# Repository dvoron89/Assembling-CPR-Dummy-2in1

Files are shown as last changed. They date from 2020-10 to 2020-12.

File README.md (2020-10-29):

# CPR-Dummy-2in1
Simulator for medical skill practicing and qualification improvement (CPR training)

Hello!
Here you can find manual for assembling CPR Dummy (look for full .doc version with images in Manual folder)

Note that you will need 3D printer (or someone who can print some models for you).

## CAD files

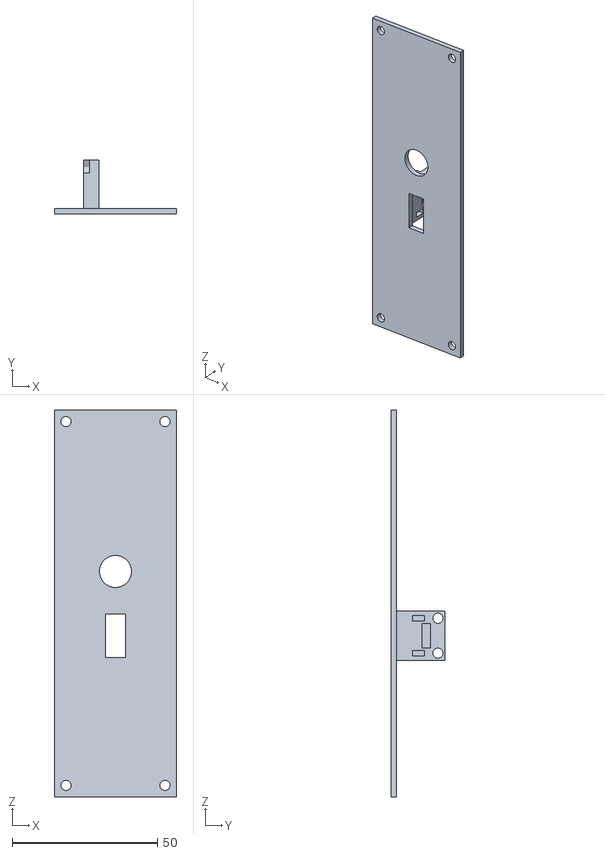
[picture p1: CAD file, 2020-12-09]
3D models to print/Large Cover (CPR195).stl
42.0 x 18.7 x 133.0

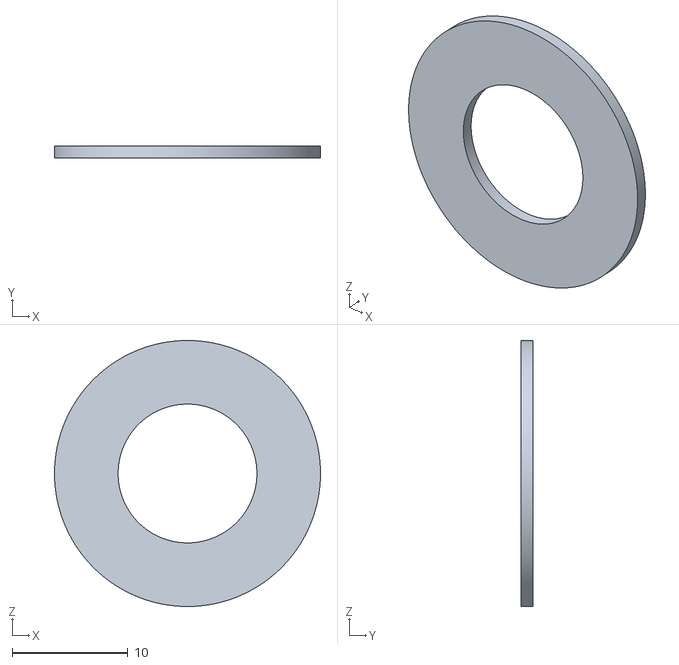
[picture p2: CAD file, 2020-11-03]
3D models to print/Inner DC Cover.stl
23.0 x 1.00 x 23.0

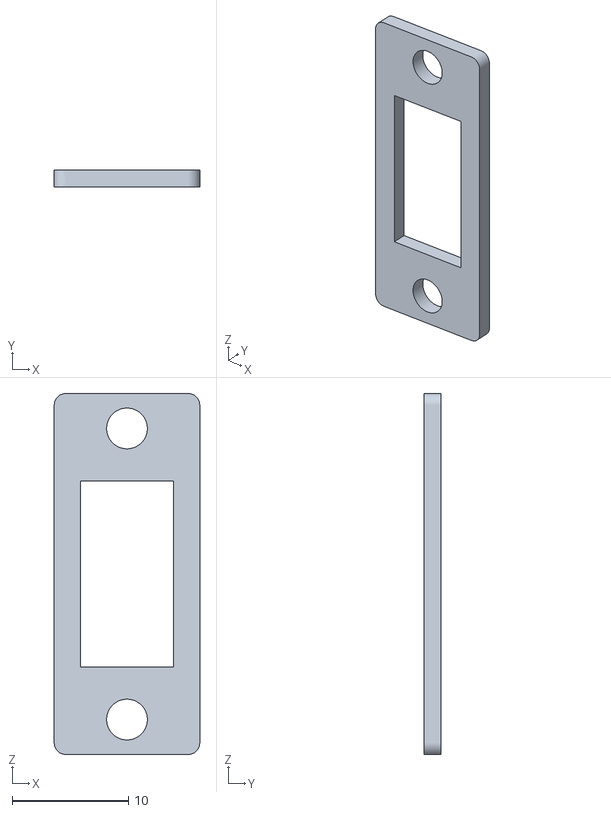
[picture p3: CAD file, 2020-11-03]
3D models to print/USB only Outer.stl
12.5 x 1.50 x 31.0

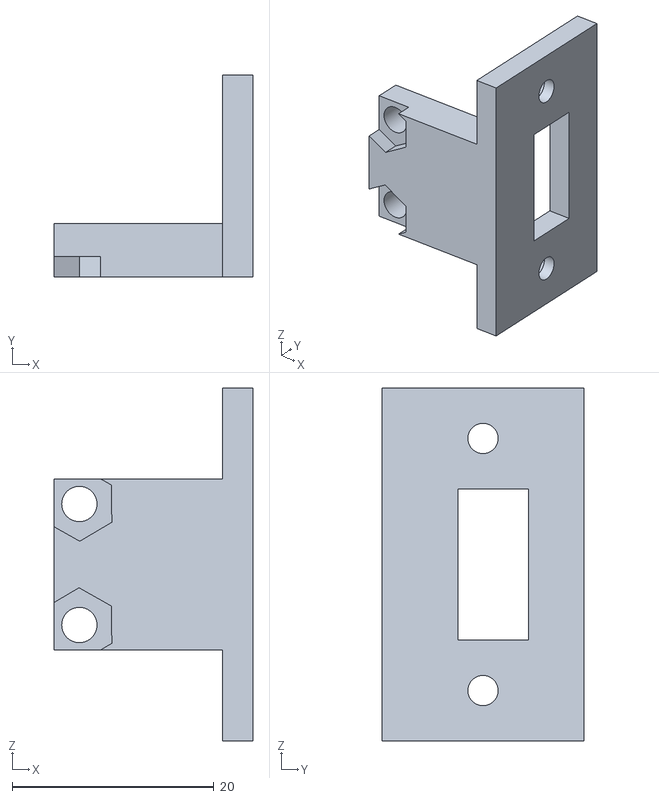
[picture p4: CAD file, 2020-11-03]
3D models to print/USB only Inner.stl
19.7 x 20.0 x 35.0

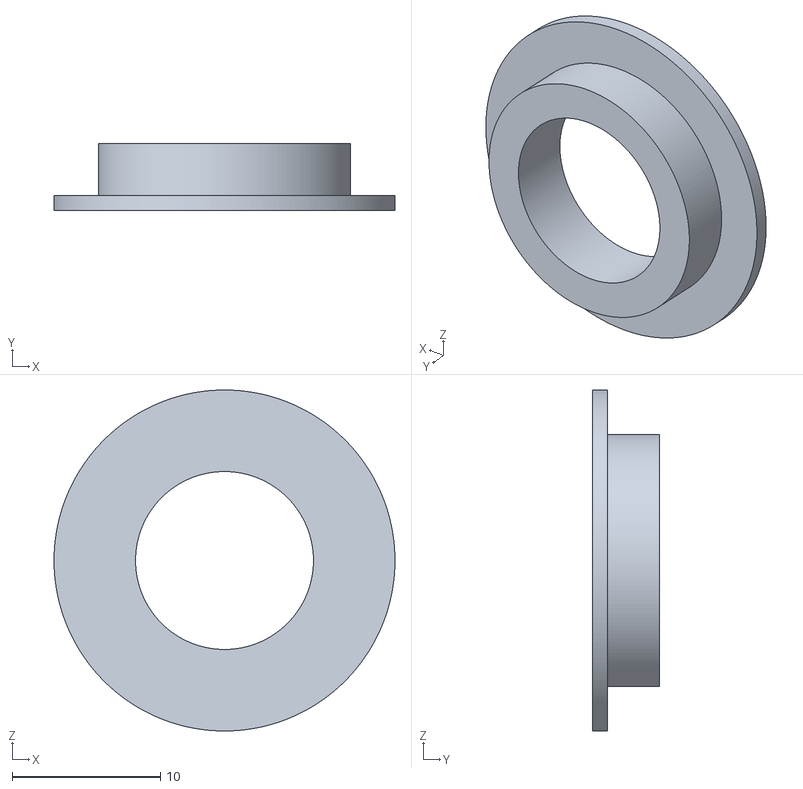
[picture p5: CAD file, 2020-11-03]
3D models to print/Outer DC Cover.stl
23.0 x 4.50 x 23.0

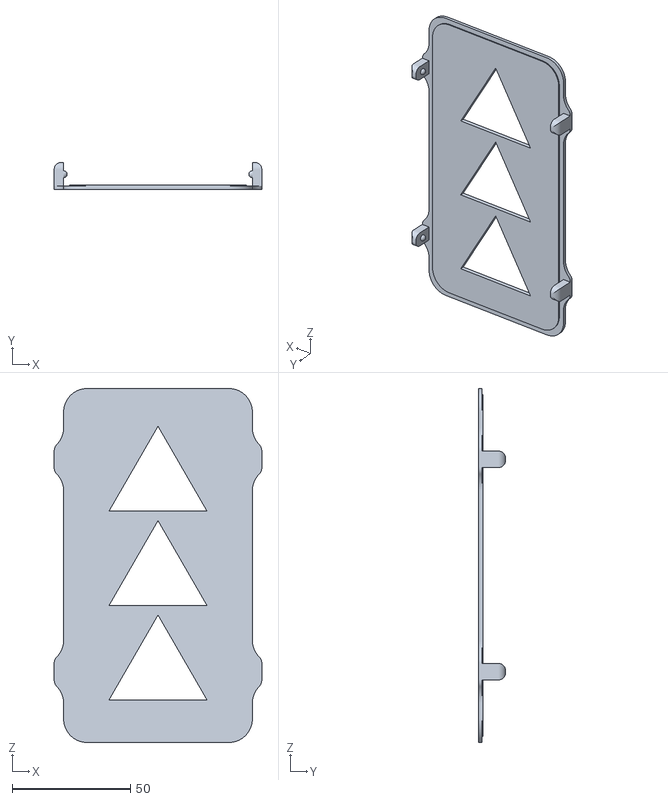
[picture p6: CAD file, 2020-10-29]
3D models to print/Custom Cover (All models).stl
88.0 x 11.5 x 150.0

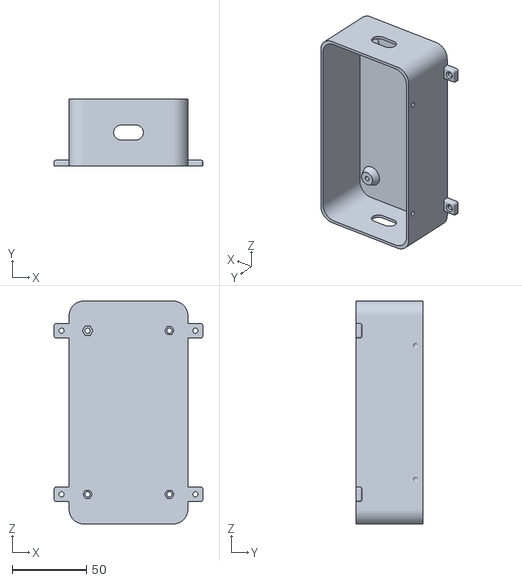
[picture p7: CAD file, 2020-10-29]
3D models to print/Case (All models).stl
100.0 x 45.0 x 150.0

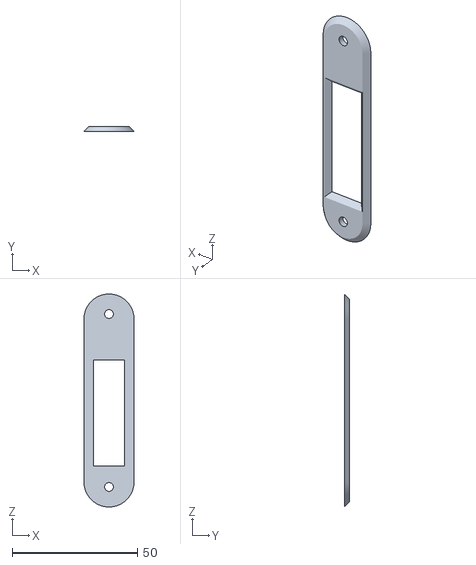
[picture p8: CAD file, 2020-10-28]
3D models to print/Outer Cover.stl
20.0 x 2.00 x 85.0

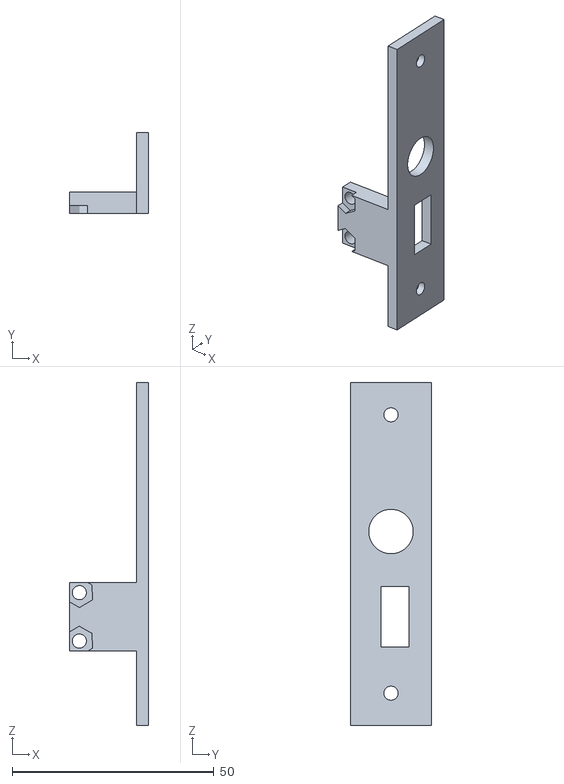
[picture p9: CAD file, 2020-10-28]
3D models to print/Inner Cover.stl
19.7 x 20.0 x 85.0

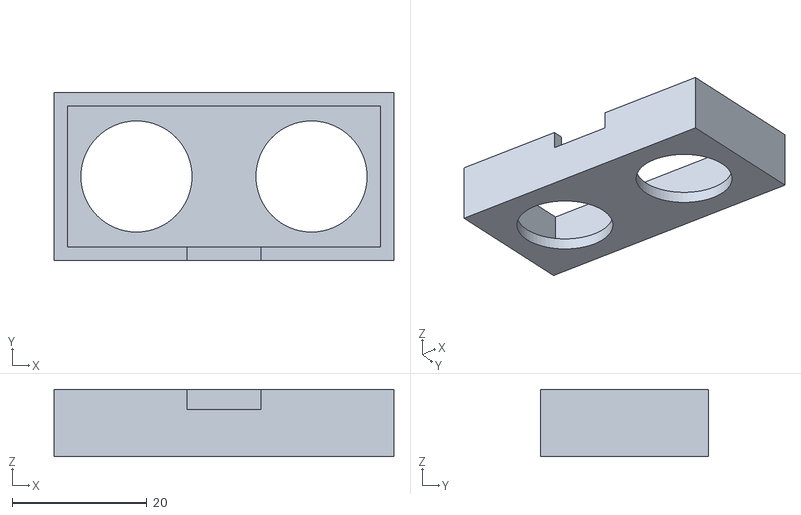
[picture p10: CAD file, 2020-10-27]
3D models to print/Sonar Case.stl
50.5 x 25.0 x 10.0

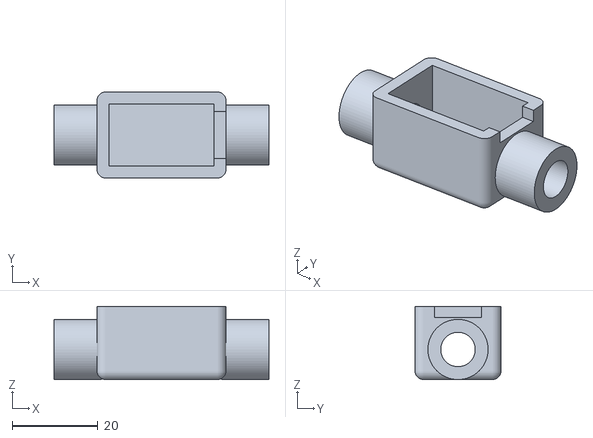
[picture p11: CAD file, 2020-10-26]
3D models to print/Pressure Sensor Case.stl
50.0 x 20.0 x 17.0

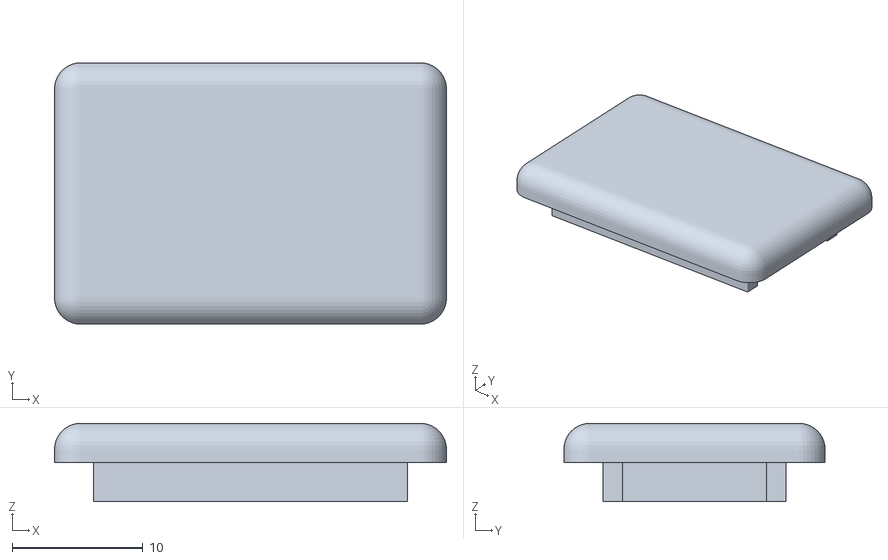
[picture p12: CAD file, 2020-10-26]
3D models to print/Pressure Sensor Cover.stl
30.0 x 20.0 x 6.00

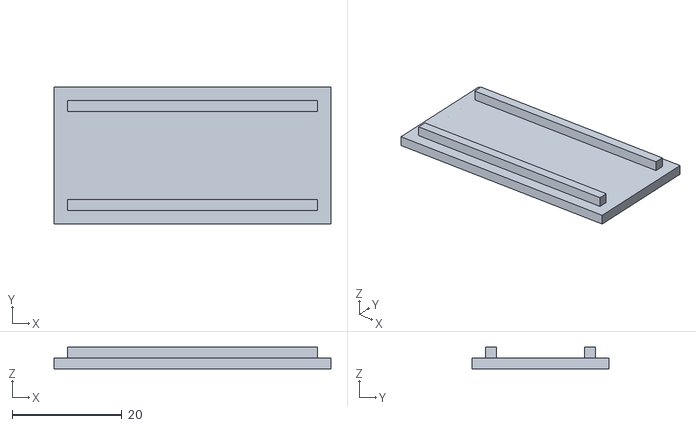
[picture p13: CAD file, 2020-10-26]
3D models to print/Sonar Cover.stl
50.5 x 25.0 x 4.00

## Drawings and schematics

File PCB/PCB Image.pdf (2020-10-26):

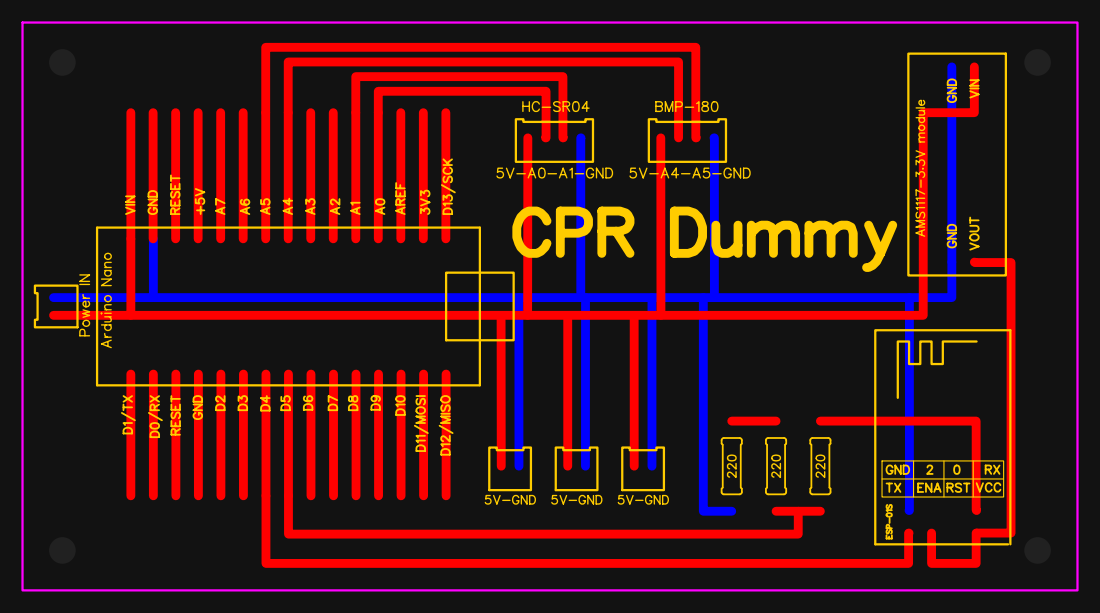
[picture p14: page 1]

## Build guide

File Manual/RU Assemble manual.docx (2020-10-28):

Инструкция по сборке симулятора для отработки СЛР с возможностью подключения к ПК по WIFI или USB кабелю

В качестве шасси применятся манекен модели CPR190 или CPR195 (предпочтительнее CPR190)

Разборка манекена:

1. Снять имитацию кожного покрова с торса манекена
2. Отсоединить трубку, имитирующую трахею/пищевод
3. Отключить все кабели, соединяющие шасси манекена с пластиной, имитирующей грудную клетку
4. Извлечь пластину, имитирующую грудную клетку из посадочного места на шасси манекена
5. При необходимости, снять имитацию кожного покрова с головы манекена и извлечь датчики из глаз и прочие электронные компоненты
6. Отключить все электронные компоненты внутри шасси манекена
7. Отсоединить и извлечь все электронные компоненты из шасси манекена
8. Извлечь перепускной клапан из разреза трубки, имитирующей трахею:

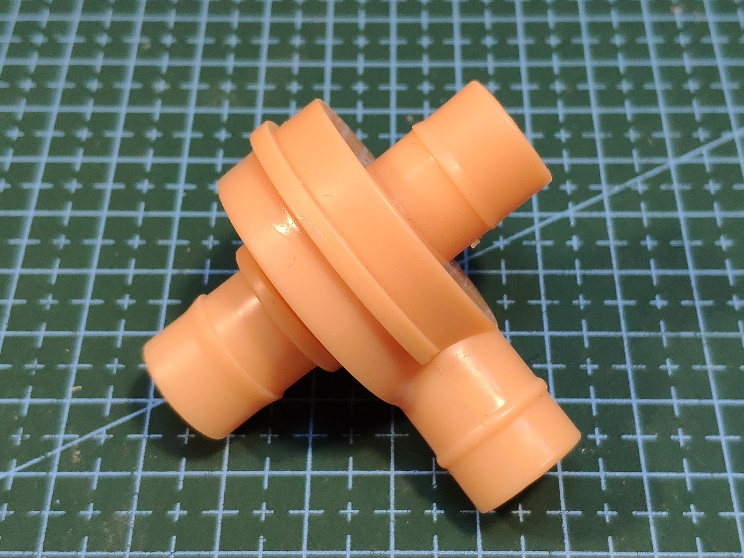
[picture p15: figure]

Подготовка шасси манекена:

1. При необходимости, удалить все выступающие части на обратной стороне кожного покрова торса:

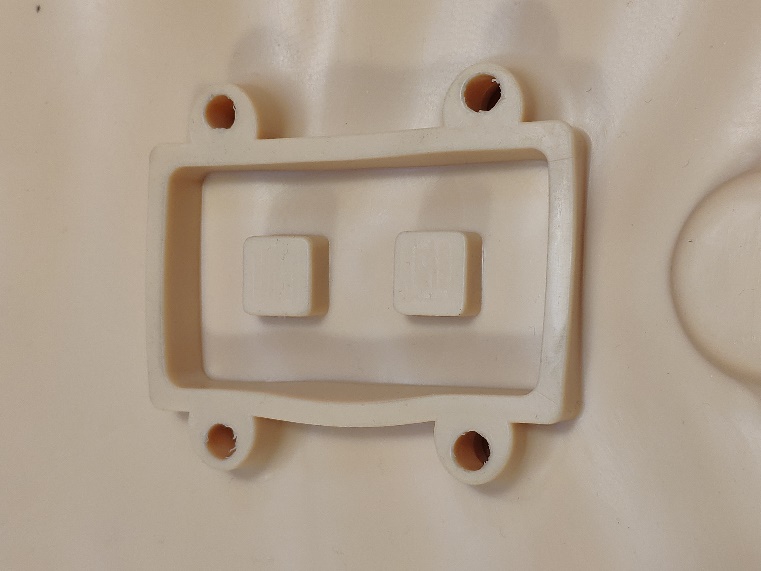
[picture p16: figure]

2. Распечатать на 3D-принтере необходимые модели. Полный список моделей по ссылке (папка 3D models to print) –

https://github.com/dvoron89/CPR-Dummy-2in1.git

- Бокс и крышка для бокса основной электронной начинки
- Бокс и крышка для бокса датчика давления
- Бокс и крышка для бокса датчика приближения
- Ответная часть для разъемов питания и USB

Подготовка электронных компонентов манекена:

1. Подготовка печатной платы:
  1.1. Распаять на плате три резистора одинакового номинала (220 Ом)
  1.2. Распаять на плате два четырехконтактных разъема для подключения дачиков и один двухконтактный разъем для подключения питания
  1.3. Распаять на плате ножки для быстрого монтажа и демонтажа Arduino, ESP-01 и регулятора напряжения (опционально)
  1.4. Разместить регулятор напряжение в посадочное место согласно разметке на плате
  1.5. Разместить Arduino Nano в посадочное место согласно разметке на плате
  1.6. Не устанавливать ESP-01 на плату до прошивки WIFI модуля
2. Подготовка датчиков:
  2.1. Подключение датчика HC-SR04:

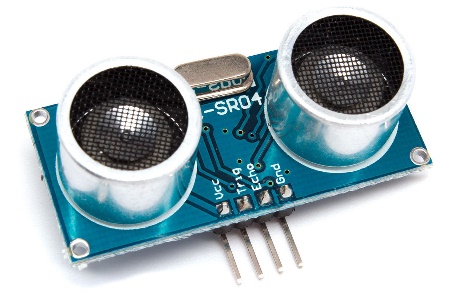
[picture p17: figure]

    - Vcc – 5V
    - Trig – A0
    - Echo – A1
    - Gnd – GND
  2.2. Подключение датчика BMP180:

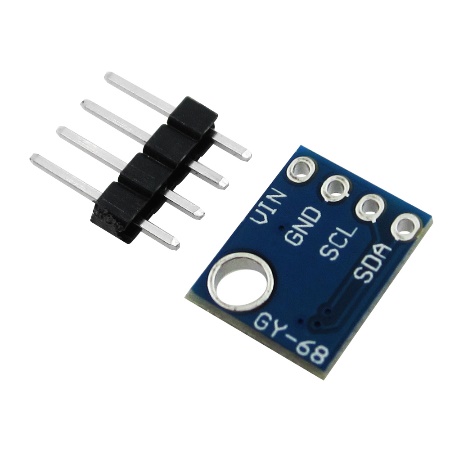
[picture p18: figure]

    - VIN – 5V
    - GND – GND
    - SCL – A5
    - SDA – A4
3. Подготовка гнезда питания:
  3.1. Распаять гнездо питания:

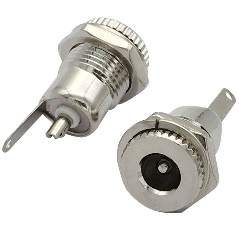
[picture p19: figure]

    - Центральный контакт на гнезде – VIN – на плате круглая точка пайки у разметки Power In
    - Крайний контакт на гнезде – GND – на плате квадратная точка пайки у разметки Power In
4. Подготовка гнезда USB type A:
  4.1. Распаять гнездо USB type A. К гнезду USB припаивается кабель USB-mini (так, кабель имеет разъемы USB-mini male – USB type A female):

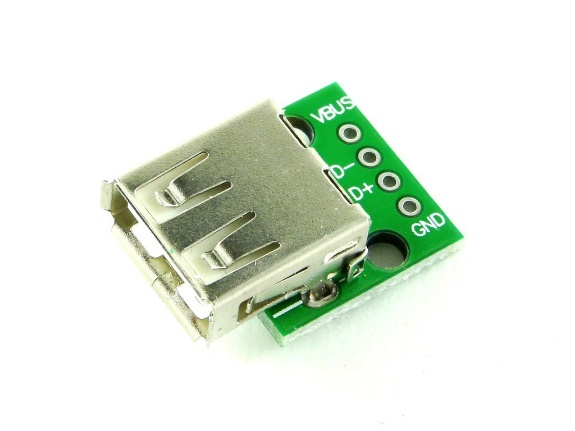
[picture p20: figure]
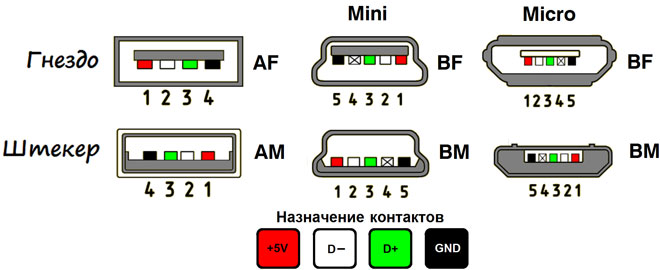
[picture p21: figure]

- VBUS – красный – 5V
- D- - белый
- D+ - зеленый
- GND - черный
5. Подготовка микроконтроллеров:
  5.1. Скачать прошивку для микроконтроллеров по ссылке (папка Firmware) –

https://github.com/dvoron89/CPR-Dummy-2in1.git

  5.2. Установить прошивку для Arduino Nano и ESP-01 соответственно. После успешной прошивки модуля ESP-01 необходимо установить его в плату на посадочное место согласно разметке

Сборка манекена:

1. Установка датчиков:
  1.1. Установить датчик BMP180 в распечатанную крышку бокса Pressure Sensor Cover. Датчик размещается в специальном углублении в крышке и фиксируется при помощи термоклеющего пистолета:

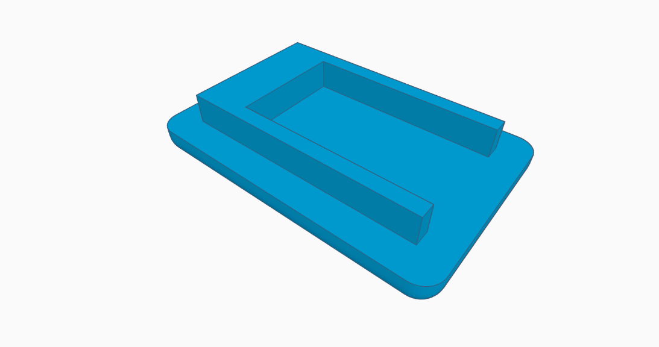
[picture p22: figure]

  1.2. Установить крышку на бокс датчика давления, вывести провода через вырез в верхней части бокса. Крышка фиксируется при помощи термоклеющего пистолета:

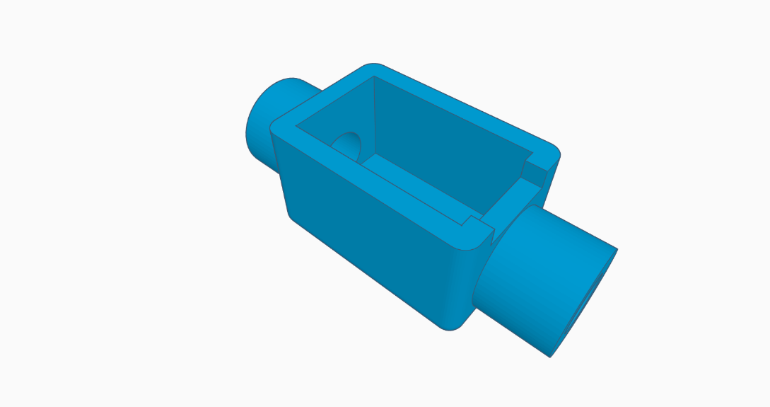
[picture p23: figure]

  1.3. Собранный бокс датчика давления устанавливается в разрез трубки, имитирующей трахею, на место ранее установленного перепускного клапана. Бокс фиксируется к трубками при помощи термоклеевого пистолета
  1.4. Установить датчик HC-SR04 в распечатанный ранее бокс для датчика приближения. Ресивер и трансмиттер на датчике должны пройти через отверстия в боксе, провода укладываеются со стороны выреза в боксе:

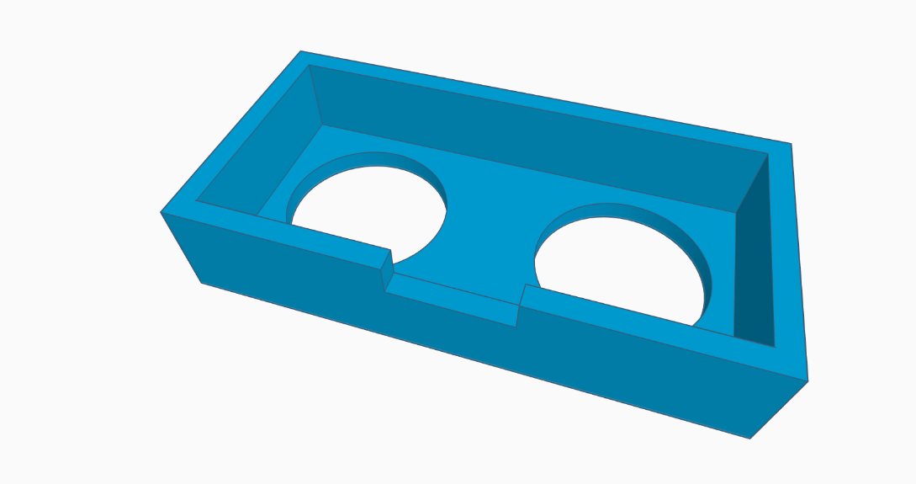
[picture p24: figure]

  1.5. Установить крышку на бокс датчика приближения и зафиксировать с помощью термоклеевого пистолета:

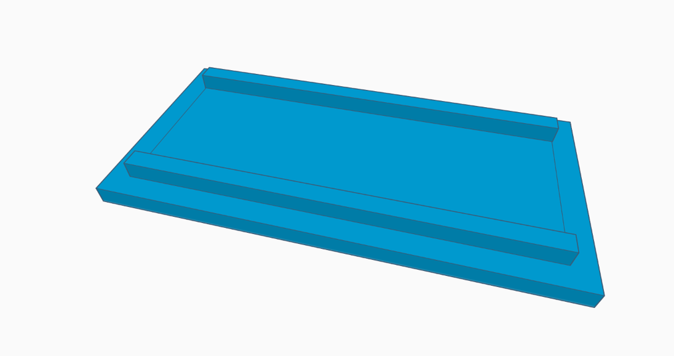
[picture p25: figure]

  1.6. Собранный бокс датчика давления установить на нижнюю сторону пластины, имитирующей грудную клетку с помощью двустороннего скотча или термоклеевого пистолета. Ресивер и трансмиттер должны смотреть строго вниз на основание шасси манекена, вдоль оси движения пластины, имитирующей грудную клетку
  1.7. Установить печатную плату в распечатанный ранее бокс для электроники манекена и зафиксировать при помощи четырех болтов и гаек М3:

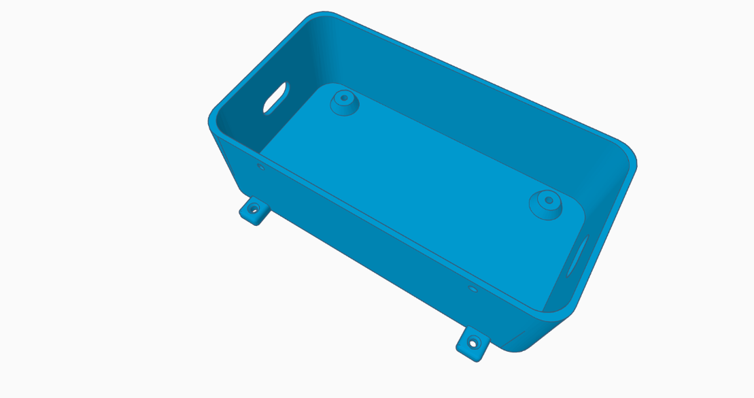
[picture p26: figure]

  1.8. Разместить бокс для электроники на нижней части основания шасси манекена и зафиксировать подходящим крепежом
  1.9. Завести провода от датчиков в бокс для электроники и подключить согласно разметке
  1.10. Подключить разъем питания к плате согласно разметке
  1.11. Подключить разъем USB-mini к Arduino Nano, установленной на плате
  1.12. Зафиксировать гнездо питания DC и гнездо USB type A на ответной части для разъемов питания и USB. Гнездо питания фиксируется собстенной комплектной гайкой. Гнездо USB фиксируется к ответной части при помощи двух болтов и гаек М3 (или М2???)
  1.13. Установить крышку на бокс для электроники

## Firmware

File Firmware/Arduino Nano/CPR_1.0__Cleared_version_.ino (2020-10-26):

#include <SFE_BMP180.h>
#include <Wire.h>
#include <SoftwareSerial.h>

#define TriggerPin A0
#define EchoPin A1

SFE_BMP180 Pressure;

SoftwareSerial ESPSerial (4, 5);

double SonarDuration;
double SonarDistance;
double SonarDistanceTraveled;
double SonarSuccessMax = 60;
int SonarDistancePercent;
double SonarInstallHeight;

double PressureMin;
double PressureMax;
double PressureNormal;
double MaxPressure = 0;
double PressureSuccesMin = 12.0;
double PressureSuccessMax = 15.0;
int PressurePercent;

String StartLine = "_";
String EndLine = ";";


void setup() 
{
  pinMode(TriggerPin, OUTPUT);
  pinMode(EchoPin, INPUT);
  
  Serial.begin(9600);
  ESPSerial.begin(9600);

  Pressure.begin();

  GetPressureNormal();
  GetSonarInstallHeight();

  delay(1000);
}

void loop() 
{
  SendDistanceData(SonarCheck());
  SendPressureData(PressureCheck());
}

void SendDistanceData(double func)
{
  Serial.println(StartLine + "D" + func + EndLine);
  ESPSerial.println(StartLine + "D" + func + EndLine);
}

void SendPressureData(double func)
{
  Serial.println(StartLine + "P" + func + EndLine);
  ESPSerial.println(StartLine + "P" + func + EndLine);
}

double SonarCheck()
{
  digitalWrite(TriggerPin, LOW);
  delayMicroseconds(5);
  digitalWrite(TriggerPin, HIGH);
  delayMicroseconds(10);
  digitalWrite(TriggerPin, LOW);

  SonarDuration = pulseIn(EchoPin, HIGH);
  SonarDistance = (SonarDuration / 2) / 2.91;
  SonarDistanceTraveled = SonarInstallHeight - SonarDistance;

  if (SonarDistanceTraveled < 0)
  {
    SonarDistanceTraveled = 0;
  }

  SonarDistancePercent = SonarDistanceTraveled / SonarSuccessMax * 100;

  if (SonarDistancePercent > 100)
  {
    SonarDistancePercent = 100;
  }
  return (SonarDistance);
}

double PressureCheck()
{
  double CurrentPressure;
  double DeltaPressure;
  CurrentPressure = getPressure();
  DeltaPressure = CurrentPressure - PressureNormal;
  if (DeltaPressure < 0)
  {
    DeltaPressure = 0;
  }

  PressurePercent = DeltaPressure / PressureSuccessMax * 100;

  if (PressurePercent > 100)
  {
    PressurePercent = 100;
  }
  return (DeltaPressure);
}

double getPressure()
{
  char status;
  double T, P, p0, a;

  status = Pressure.startTemperature();
  if (status != 0)
  {
    // ожидание замера температуры
    delay(status);
    status = Pressure.getTemperature(T);
    if (status != 0)
    {
      status = Pressure.startPressure(3);
      if (status != 0)
      {
        // ожидание замера давления
        delay(status);
        status = Pressure.getPressure(P, T);
        if (status != 0)
        {
          return (P);
        }
      }
    }
  }
}

void GetPressureNormal()
{
  PressureNormal = getPressure();
}

void GetSonarInstallHeight()
{
  digitalWrite(TriggerPin, LOW);
  delayMicroseconds(5);
  digitalWrite(TriggerPin, HIGH);
  delayMicroseconds(10);
  digitalWrite(TriggerPin, LOW);

  SonarDuration = pulseIn(EchoPin, HIGH);
  SonarInstallHeight = (SonarDuration / 2) / 2.91;
}

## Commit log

2020-10-26 3D models update
    Sonar cover model uploaded;
    Pressure sensor cover model uploaded;
    [Pressure Sensor Case.stl, Pressure Sensor Cover.stl, Sonar Case.stl, Sonar Cover.stl]
2020-10-26 PCB added
    PCB image and gerber uploaded
2020-10-26 Microcontrollers firmware uploaded
    - Arduino Nano firmware added;
    - ESP-01 firmware added;
2020-10-27 3D model update
    - Sonar Case model updated;
    [Sonar Case.stl]
2020-10-28 3D models update
    - Side cover for USB and DC ports added;
    [Inner Cover.stl, Outer Cover.stl]
2020-10-29 3D models update
    - 3D models for case and cover added;
    [Case.stl, Custom Cover.stl]
2020-11-03 3D models update
    - Models for single DC port added;
    - Models for single USB port added;
    [Inner DC Cover.stl, Outer DC Cover.stl, USB only Inner.stl, USB only Outer.stl]
2020-11-03 Firmware update
    Arduino Nano update ver 1.1:
    - Sonar sensor now sends distance traveled instead of distance from dead point;
2020-12-09 3D models update
    - Large cover for CPR195 added;
    [Case (All models).stl, Custom Cover (All models).stl, Large Cover (CPR195).stl]
